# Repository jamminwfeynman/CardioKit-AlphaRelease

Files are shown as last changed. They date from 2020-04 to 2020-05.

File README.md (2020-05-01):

# CardioKit-AlphaRelease
The public release of these and many more documents is a very active work in progress. The files currently present are enough to manufacture and operate the platform. That said, I am still working on documenting all of my 'institutional knowledge' that I know is just as necessary for making the platform operate as it should. 

Please feel free to reach out if you have an urgent application or desire to collaborate in the meantime.

<p align="center">
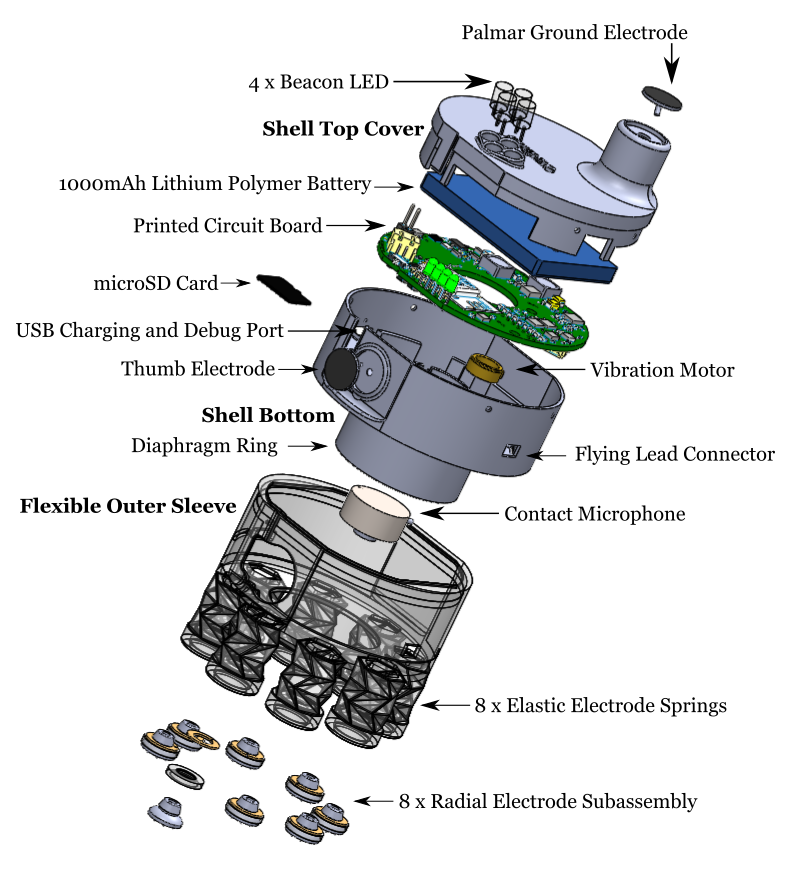
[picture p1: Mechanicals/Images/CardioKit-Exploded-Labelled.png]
  

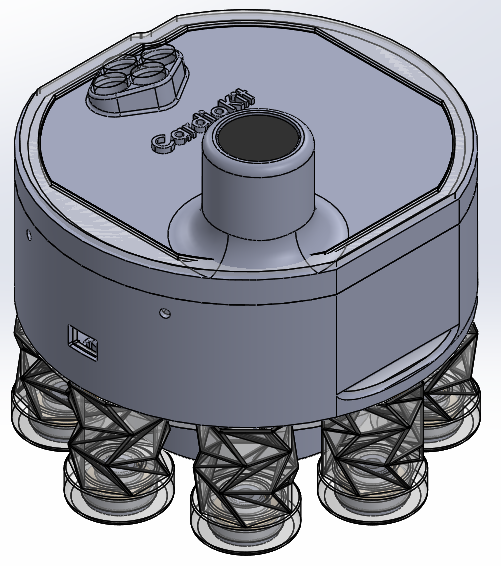
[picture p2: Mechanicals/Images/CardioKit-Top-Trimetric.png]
  

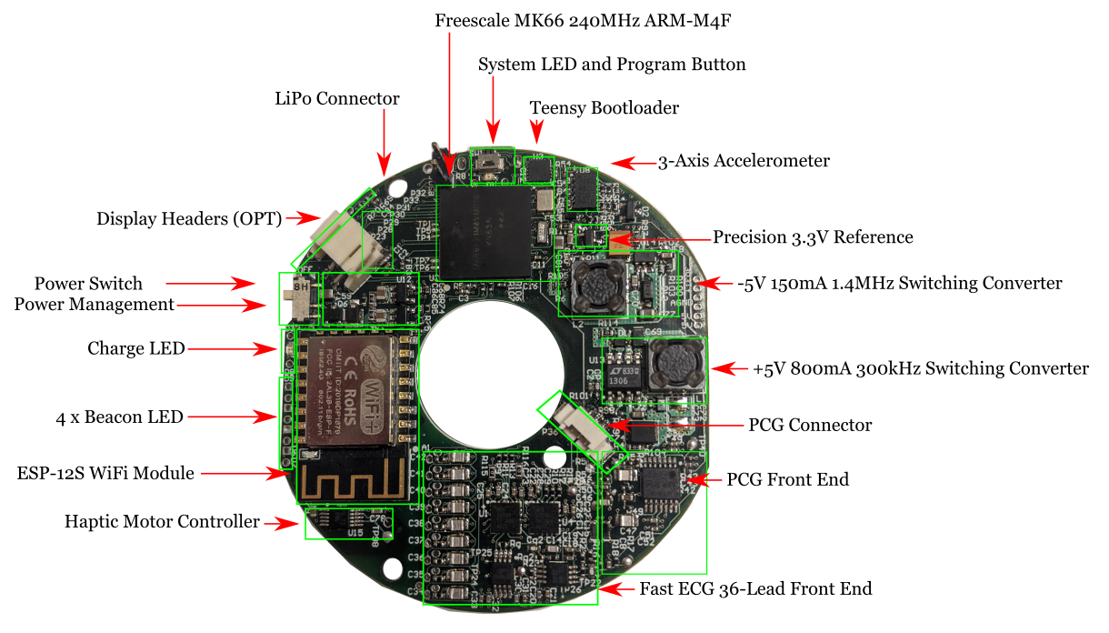
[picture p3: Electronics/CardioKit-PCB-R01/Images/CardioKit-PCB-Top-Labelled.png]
  

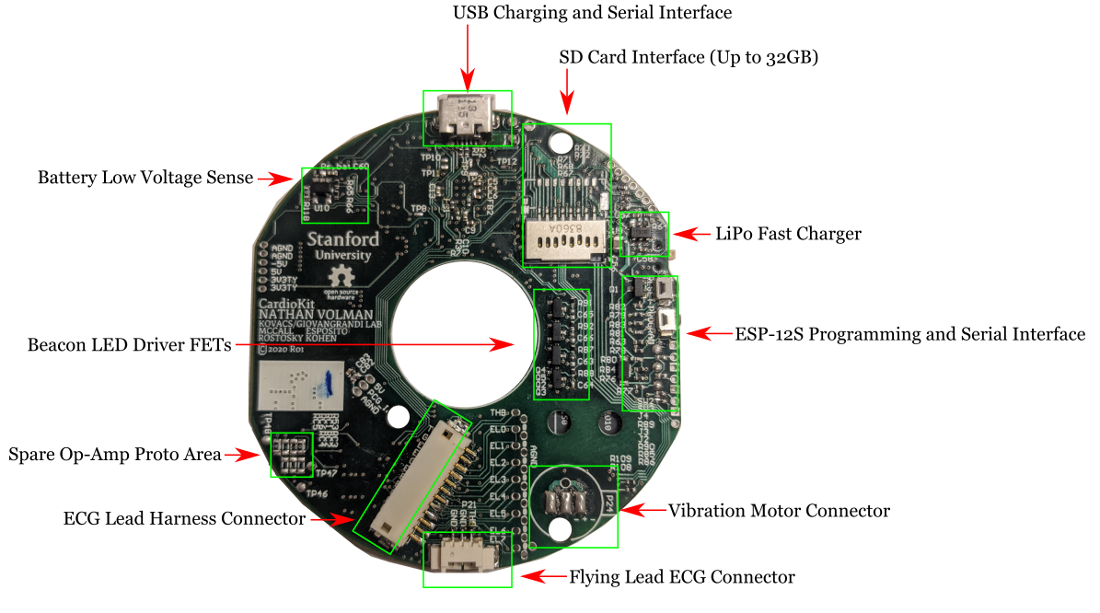
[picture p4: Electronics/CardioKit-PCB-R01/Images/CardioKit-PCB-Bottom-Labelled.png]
  
</p>

## Quickstart Guide
- Order the CardioKit PCB R10 with assembly services using the parts in the BOM. These should be 1.6mm thick and use ENIG surface plating. Order quantity 1 per finished device.
- Order PCB Electrode Holders along with the main PCB. These should be 0.6mm thick and use ENIG surface plating. Order quantity 10 per finished device.
- Using FormLabs Form 2 with Elastic Resin or a 3D printing service with access to the same, per device print one Flexible Sleeve and eight Flexible Electrode Holders. These can be printed at the same time and also in batches of at least 2 sets at a time using the Form 2.
- Using FormLabs Form 2 with any colored resin of your choice (e.g. Grey Resin) or a 3D printing service with access to the same, per device print one Bottom Shell and one Top Shell. These can be printed at the same time and also in batches of at least 2 sets at a time using the Form 2.
- Using the Arduino IDE, Atom with PlatformIO, or your favorite C/C++ IDE import the CardioKit Firmware and upload it to each device over the USB port. Note: you will need to have Teensyduino installed before uploading.
- Following the instructions in the readme, flash the ESP8266 module with esp-link. This will require an FTDI cable attached to the ESP8266 programming headers on the underside of the PCB.
- Assemble PCB, sensors, battery, vibration motor, and housing together into the completed device. (More detailed build guide coming soon).
- For local network use: Using Processing of Java Eclipse, import the CardioKit Host Software. With the device enabled, enter its IP address and run the software to automatically connect.
- For cloud use: Spin up an instance on AWS and follow the directions above. Note: you may need to bypass your network's firewall to successfully connect. (More details coming soon).
- That's it! All signals recorded by the device will be stored in a csv for post-processing at the end of each session. Example signal importation and post-processing can be seen in this Matlab script.

## To-Do
- Clean-up, optimization, repackaging of firmware
- Clean-up, optimization, repackaging of cloud software
- Detailed description of performance and capabilities
- Detailed build guide
- Tips for self-assembly of pcb and sourcing of parts
- Initial commits of most of the post-processing code
- Tips for getting good results from 3D printer and description of process
- Detailed guide for extending FW/SW/HW/Mechanicals
- Much more...

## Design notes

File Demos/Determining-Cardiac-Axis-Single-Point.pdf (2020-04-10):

## Determining Cardiac Axis from a Single Point

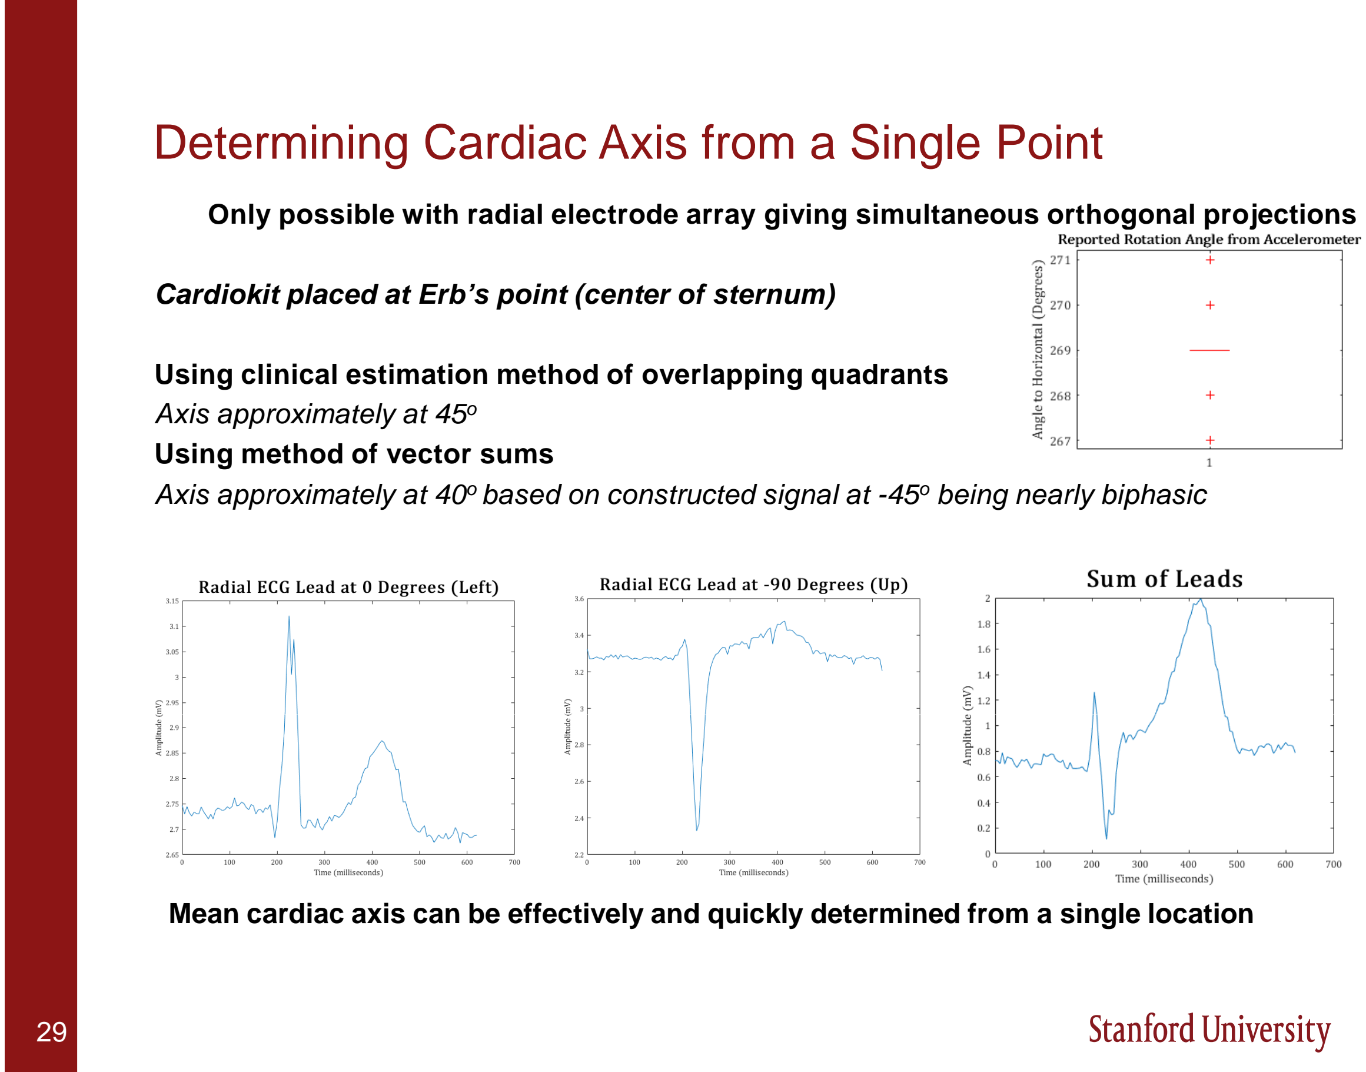
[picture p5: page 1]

Only possible with radial electrode array giving simultaneous orthogonal projections

Cardiokit placed at Erb’s point (center of sternum)

Using clinical estimation method of overlapping quadrants
Axis approximately at 45
o
Using method of vector sums
Axis approximately at 40o based on constructed signal at -45

o being nearly biphasic

29

Mean cardiac axis can be effectively and quickly determined from a single location

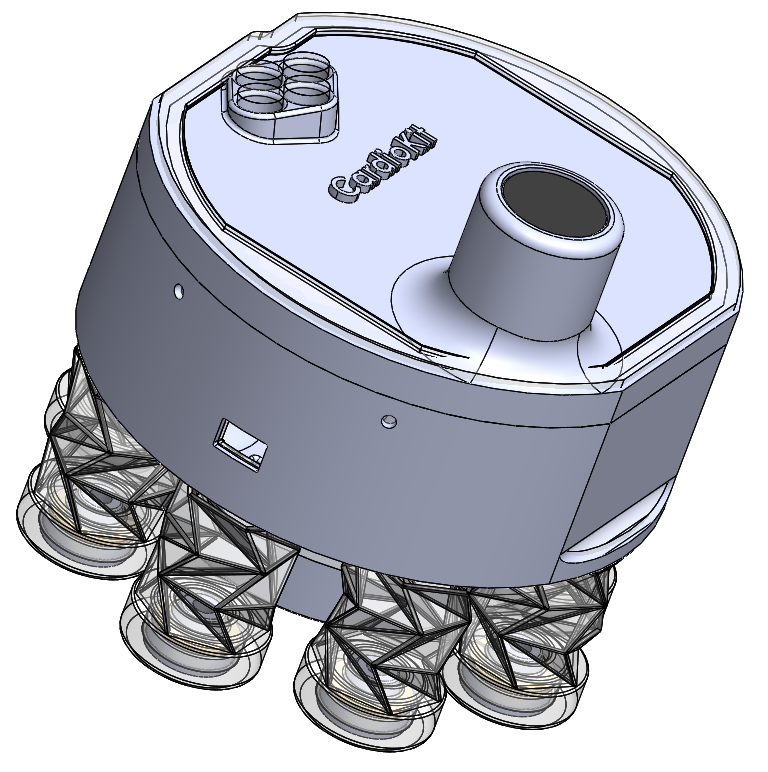
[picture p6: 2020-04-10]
Mechanicals/Images/CardioKit-Top.png

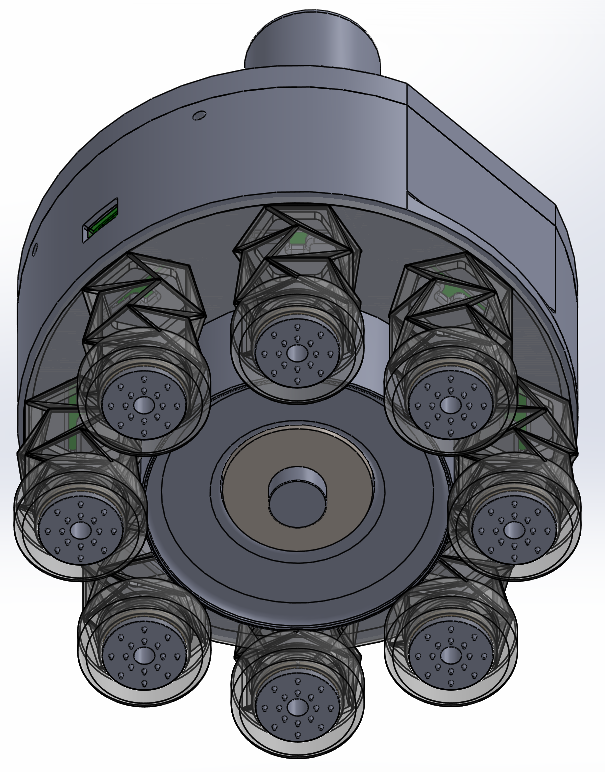
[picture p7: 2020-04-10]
Mechanicals/Images/CardioKit-Bottom-Trimetric.png

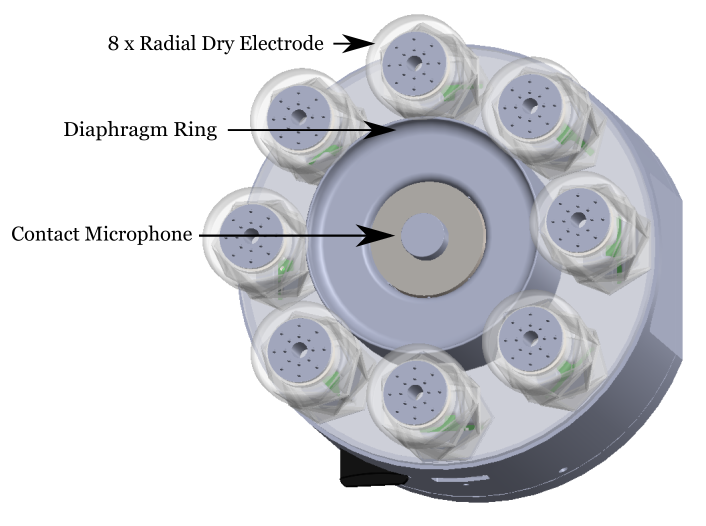
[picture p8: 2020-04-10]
Mechanicals/Images/CardioKit-Bottom-Labelled.png

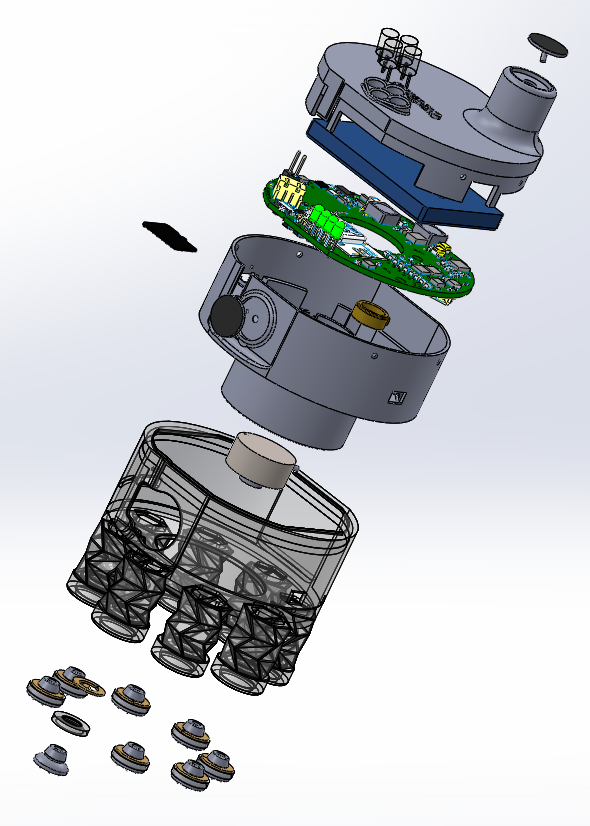
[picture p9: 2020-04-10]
Mechanicals/Images/CardioKit-Exploded.png

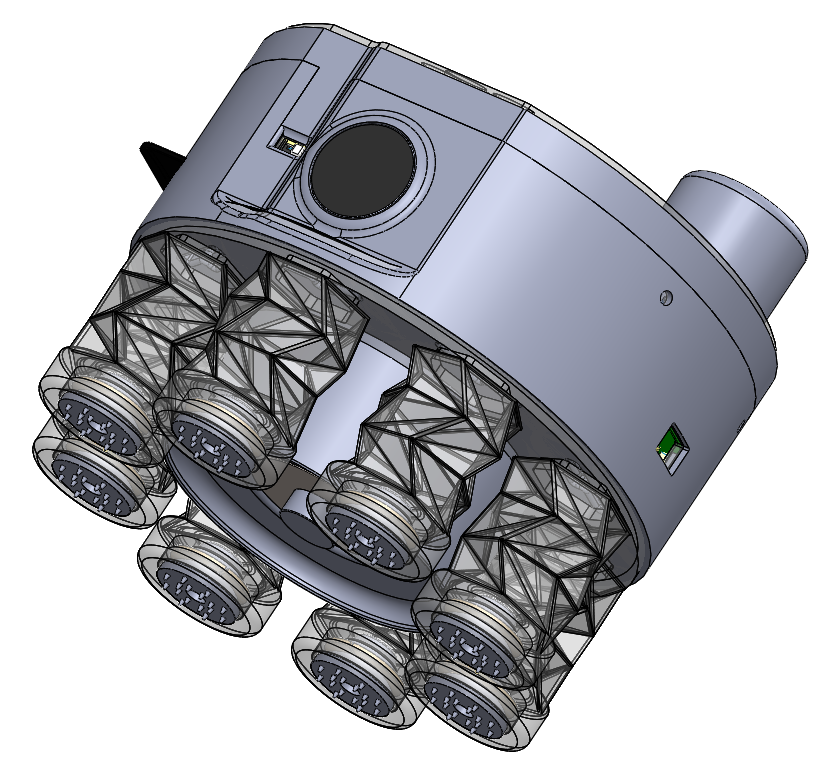
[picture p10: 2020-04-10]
Mechanicals/Images/CardioKit-Thumb-Side.png

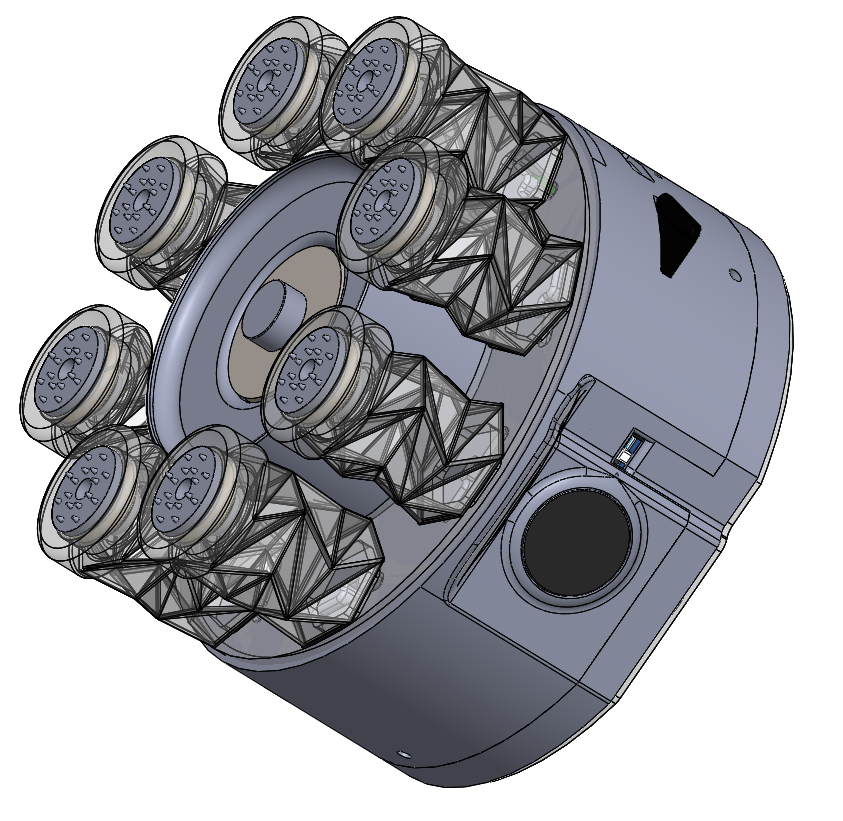
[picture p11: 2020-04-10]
Mechanicals/Images/CardioKit-PCG-Electrodes.png

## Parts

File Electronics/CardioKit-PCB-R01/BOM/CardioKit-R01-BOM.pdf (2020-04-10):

Comment | Description | Designator | Manufacturer Part Number | Quantity
0.1uF | CL05 Series 0.1 uF 16 V ±10% Tolerance X7R SMT Multilayer Ceramic Capacitor

C1, C4, C8, C10, C11, C12, C13, C19, C21, C23, C25, C27, C29, C31, C33, C43, C50, C52, C54, C55, C57, C58, C60, C63, C64, C65, C66, C75, C83, C84, C85, C86

CL05B104KO5NNNC | 32
110pF 5% C0G | CAP CER 110PF 50V 5% NP0 0402 | C7, Cg2 | C0402C111J5GAC7867 | 2
2nF 5% C0G | CAP CER 2000PF 50V 5% NP0 0603 | C14, C46 | GRM1885C1H202JA01D | 2
100pF | Cap Ceramic 100pF 50V C0G 5% SMD 0402 125°C Cardboard T/R | C18, C20, C22, C24, C26, C28, C30, C32, C49, C51, C82 | CL05C101JB5NNNC | 11
10nF 16V 2% PPS | Capacitor 0.01 uF 16 Volt PLYPH 2% 2 X 1.25 X 1.1mm Surface Mount Tape and Reel | C34, C35, C36, C37, C38, C39, C40, C41, C42, C44, C47 | ECH-U1C103GX5 | 11
15nF 5% | CAP CER 0.015UF 35V NP0 0603 | C45 | C1608C0G1V153J080AC | 1
240pF 5% C0G | Multilayer Ceramic Capacitors MLCC - SMD/SMT 240pF 50Volts C0G 2% | C48 | C0402C241J5GAC7867 | 1
10uF 16V | Cap Multilayer Ceramic 0805 10uF 16V ±10% X7R CL21 Series | C56, C59, C62, C67, C81 | CL21B106KOQNNNG | 5
1uF 16V | CAP CER 1UF 16V X7R 0603 | C70, C76, C78, C79, C80 | CL10B105MO8NNWC | 5
22uF Tant | Cap Tant Solid 10uF 10V B CASE 10% (3.5 X 2.8 X 1.9mm) Inward L SMD 3528-21 2.5 Ohm 125C T/R | C71 | TAJB106K010RNJ | 1
220uF | Cap Tant Solid 220uF 6.3V B CASE 20% (3.5 X 2.8 X 1.9mm) SMD 3528-21 0.045 Ohm 105°C T/R | C72, C74 | T520B227M006ATE045 | 2
68pF | Cap, 68Pf, 25V, 5%, C0g/Np0, 0402 | CP | 8.85E+11 | 1
68nF | Cap Cer 0.068UF 16V X7R 0402 | CZ | CC0402KRX7R7BB683 | 1
1200pF 10% | CAP CER 1200PF 100V 5% X7R 0603 | C_NFB | CL10B122KB8NNNC | 1
BAV70LT1G | Dual Switching Diodes, Common Cathode, 3-Pin SOT-23, Pb-Free, Tape and Reel | D2 | BAV70LT1G | 1
MBR120 | MBR120LSFT Series 20 V 1 A Surface Mount Schottky Power Rectifier - SOD-123FL | D5 | MBR120LSFT1G | 1
Bourns SRF0703-220M | Ind Power Shielded Wirewound 10uH/40uH 20% 100KHz Ferrite 2.08A/1.04A T/R | L1, L2 | SRF0703-220M | 2
Hirose DF13-12P-1.25H(76) | DF13 Series 12 Position Single Row 1.25 mm Right Angle SMT Pin Header | P6 | DF13-12P-1.25H(76) | 1
Molex 53261-0371 | Conn Shrouded Header HDR 3 POS 1.25mm Solder RA SMD PicoBlade Embossed T/R | P21, P36 | 53261-0371 | 2
RK7002BM | N-Channel 60 V 0.2 W Surface Mount 2.5 V Drive Silicon Power Mosfet - SOT-23 | Q1, Q2, Q3, Q4, Q5 | RK7002BMT116 | 5
0R | Res Thick Film 0603 0 Ohm Molded SMD SMD Punched Carrier T/R | R4, R6, R53, R54, R69, R70, R94, R97,
| | R110, R111, R113, R114, R115, R116,
| | R117, R118, RC5 | ERJ-3GEY0R00V | 17
1k 1% | YAGEO (PHYCOMP) RC0402FR-071KL RESISTOR, RC32H 0402 1K

R9, R10, R11, R12, R13, R14, R44, R55,
R57, R58, R59, R61, R62, R67, R68, R71,
R72, R73, R74, R76, R77, R82, R87, R88, R91, R92, R108, R109
RC0402FR-071KL | 28
10k2 1% | Thick Film Resistors - SMD 10.2K OHM 1% | R15, Rg2 | RC0402FR-0710K2L | 2
3k4 1% | Thick Film Resistors - SMD 3.4K OHM 1% | R16 | RC0402FR-073K4L | 1
17k8 1% | Thick Film Resistors - SMD 17.8K OHM 1% | R17 | RC0402FR-0717K8L | 1
10k7 1% | RES SMD 10.7K OHM 1% 1/16W 0402 | R18 | RC0402FR-0710K7L | 1
442R 1% | Thick Film Resistors 442 OHM 1% | R21, R22 | RMCF0402FT442R | 2
560R 1% | RES SMD 560 OHM 1% 1/16W 0402 | R23 | RC0402FR-07560RL | 1
100k 0.1% | RES SMD 100K OHM 0.1% 1/16W 0402 | R24, R25, R26, R27, R28, R29, R30, R31, R32, Rs,bat | RNCF0402DTE100K | 10
162k 1% | Thick Film Resistors - SMD 0402 162Kohms 1% Tol | R42, R43, R51 | RC0402FR-07162KL | 3
4k42 1% | Thick Film Resistors - SMD 4.42K OHM 1% | R45, R48, R50 | RC0402FR-074K42L | 3
6k65 1% | Thick Film Resistors 6.65K OHM 1% | R49 | RC0402FR-076K65L | 1
232k 1% | Thick Film Resistors - SMD 0402 232Kohms 1% Tol | R52 | RC0402FR-07232KL | 1
10k | Res Thin Film 0402 10K Ohm 0.5% 0.063W(1/16W) ±25ppm/C Molded SMD Automotive Punched T/R | R56, R60, R65, R75, R78, R79, R80, R81, R83, R84, R95, R102, R103 | RMCF0402FT10K0 | 13
2k2 5% | RES SMD 2.2K OHM 5% 1/16W 0402 | R63, R106, R107 | RC0402JR-072K2L | 3
1k1 | RES SMD 1.1K OHM 1% 1/16W 0402 | R64 | CRCW04021K10FKED | 1
1M65 1% | Thick Film Resistors - SMD 1.65M OHM 1% | R66 | RMCF0402FT1M65 | 1
91R 5% | Thick Film Resistors - SMD 91 OHM 5% | R85, R86, R89, R90 | RMCF0402JT91R0 | 4
768k | Thick Film Resistors - SMD 0402 768Kohms 1% Tol | R98 | ERJ-2RKF7683X | 1
249k | RES SMD 249K OHM 1% 1/16W 0402 | R99 | MCR01MRTF2493 | 1
29k4 | Thick Film Resistors - SMD 29.4K OHM 1% | R100 | RC0402FR-0729K4L | 1
118k | RES SMD 118K OHM 1% 1/16W 0402 | R101 | CRCW0402118KFKED | 1

100R 5% 1/4W | Res Thick Film 0603 100 Ohm 5% 1/4W +/-200ppm/ßC Molded SMD SMD Paper T/R | R104, R105 | ESR03EZPJ101 | 2
1k5 0.1% | RES SMD 1.5K OHM 0.1% 1/16W 0402 | Rg | RT0402BRD071K5L | 1
MUX36S08 | 36-V, low-capacitance, low-leakage-current, precision, analog multiplexer 16-WQFN -40 to 125 | U1, U4 | MUX36S08IRRJR | 2
OPA2141 | 10 MHz, Single Supply, Low Noise, JFET Precision Amplifier, 4.5 to 36 V, -40 to 125 degC, 8-pin SOP (DGK8), Green (RoHS & no Sb/Br) | U5 | OPA2141AIDGKT | 1
AD8220 | SP Amp Instrumented Amp Single Rail to Rail O/P ±18 Volt 36 Volt 8-Pin MSOP | U6 | AD8220BRMZ | 1
OPA4141 | 10 MHz, Single Supply, Low Noise, JFET Precision Amplifier, 4.5 to 36 V, -40 to 125 degC, 14-pin SOP (PW14), Green (RoHS & no Sb/Br) | U7 | OPA4141AIPW | 1
ADXL345 | 3-Axis, +/-2 g / +/-4 g / +/-8 g / +/-16 g Digital Accelerometer with Digital Output, 1.6 KHz BW, Industrial, 14-
| pin LGA, Tray | U8 | ADXL345BCCZ | 1
MIC7221 | MIC7221 Series Single 10 V 0.5 pA IttyBitty? Rail-to-Rail Comparator - SOT-23-5 | U10 | MIC7221 | 1
DRV2605L | Haptic Driver for ERM and LRA with Built-In Library and Smart Loop Architecture 10-VSSOP -40 to 85 | U15 | DRV2605L | 1
REF3333AIDBZR | 30 ppm / degC Drift, 3.9 uA Voltage Reference, -40 to 125 degC, 3-pin SOT-23 (DBZ), Green (RoHS & no Sb/Br) | U16 | REF3333AIDBZR | 1
3-Terminal Pico Blade Female Wire-To-Board | | | ?0510210300? | 2
Pico Blade Crimp Connector | | | ?0500588000? | 6
Hirose Female Wire-To-Board | | | DF13-12S-1.25C? | 1
Hirose Low Insertion Force Gold Crimp Pin | | | DF13G-2630SCFA? | 12
LED | LED; Red; 30mcd; 0.126In.Dia.; T-1; 150mA; 2V; 635nm; 60deg; Diffused; 85 to 85degC | D4, D6, D7, D8, D9 | OVLLR8C7 | 5
ESP-12S | ESP-12S | A1 | | 1
CM-01B
100k DNP | THIN FILM, RESISTOR, 100KOHM, 63mW, ±0.5% | R5 | ERA-2AED104X | 1
10M 1% | YAGEO (PHYCOMP) RC0402FR-0710ML RESISTOR, 0402 0.063W 1% 10M | R33, R34, R35, R36, R37, R38, R39, R40, R41 | RC0402FR-0710ML | 9
310-105 | Precision Microdrives 310-105 10mm Vibration Motor - 4mm Type | P24 | 310-105 | 1
Omron B3U-3000P | TACTILE SWITCH, SIDE ACTUATED, SMD | SW1,SW2,SW3 | B3U-3000P | 1
MKL02Z32VFG4 | 32 Bit Microcontroller, Kinetis L Series Ultra Low Power, ARM Cortex-M0+, 48 MHz, 32 KB, 4 KB, 16 | U3 | MKL02Z32VFG4 | 1
LiPo | 2 Positions Header, Shrouded Connector 0.079 (2.00mm) Surface Mount | BT1 | S2B-PH-SM4-TB(LF)(SN) | 1
Microsemi UPS115UE3/TR7 | Standard Recovery Diode And Rectifier | D10 | UPS115UE3/TR7 | 1
33R | Thick Film Resistors - SMD 1/16W 33ohm 1% | R1, R2 | AC0402FR-0733RL | 2
120 | Chip Ferrite Bead for Power Lines, 120 Ohm, 2000 mA, -55 to 125 degC, 1 x 0.5 x 0.55 mm SMD, Tape and Reel | FB3, FB4 | BLM15PX121SN1D | 2
600 | Chip Ferrite Bead for Power Lines, 600 Ohm, 900 mA, -55 to 125 degC, 1 x 0.5 x 0.55 mm SMD, Tape and Reel | FB1, FB2 | BLM15PX601SN1D | 2
470R | Thick Film Resistors - SMD 0402 470ohms 5% Tol, Thick Film Resistors - SMD 0402 470ohms 5% Tol, RES SMD 470 OHM 1% 1/16W 0402 | R3, R7, R8 | ERJ-2GEJ471X, ERJ-2GEJ471X, CRCW0402470RFKED | 3
32.768kHz | Crystal 0.032768MHz ±20ppm (Tol) 12.5pF Flexural 50000Ohm 2-Pin SMD T/R | X2 | TFE322P32K7680R | 1
LT1306 | LT1306 - Synchronous, Fixed Frequency Step-Up DC/DC Converter | U13 | | 1
LT1611 | Inverting 1.4 MHz Switching Regulator, 5-pin SOT23 (S5-5), 0 to 70 degC, Pb-Free, Tape and Reel | U14 | LT1611CS5#TRPBF | 1
NXP Semiconductors MK66FX1M0VMD18 | Kinetis K66: 180MHz Cortex-M4F MCU, 1.2MB Flash, 256KB SRAM, 2xUSB, Ethernet, 144-MAPBGA | U2 | MK66FX1M0VMD18 | 1
BQ21040 | 0.8A Single Input Single-Cell Li-Ion and Li-Pol Battery Charger 6-SOT-23 0 to 125 | U9 | | 1
16MHz | CRYSTAL 16MHZ 8PF SMD | X1 | NX3225SA-16.000MHZ-STD-CSR-1 | 1
Micro SD Card Connector | Conn Micro SD Card HDR 8 POS 1.09mm Solder RA SMD Embossed T/R 0.5A | P1 | 1051620001 | 1
1uF | Cap Tant Polymer 1uF 35VDC W9 CASE 20%( 2 X 1.25 X 0.9mm) SMD 2012-09 0.5 Ohm 105C T/R | C69 | T58W9105M035C0500 | 1
MMDL914T3G | High-Speed Switching Diode, 2-Pin SOD-323, Pb-Free, Tape and Reel | D11 | MMDL914T3G | 1
MBR0520 | Rectifier, Schottky Power; Plastic Sod-123; 0.5 a @ +90c If; +125; 20v; 1000 | D12 | MBR0520LT1G | 1
22uF | Cap Tant Polymer 22uF 10VDC M CASE 20%( 1.6 X 0.85 X 1mm) Undertab SMD 1608-09 0.5 Ohm 60C T/R | C73 | F381A226MMAAXE | 1
22uF 6.3V | Cap Ceramic 22uF 6.3V X5R 10% SMD 0805 85°C Cardboard T/R | C77 | CL21A226KQCLRNC | 1
SSM3J328R | Trans MOSFET P-CH Si 20V 6A 3-Pin SOT-23F | Q6 | SSM3J328R | 1
LP5907QMFX-3.3 | IC REG LDO 3.3V 0.25A SOT23-5 | U11, U12 | LP5907MFX-3.3/NOPB | 2
CUS-12TB | Switch Slide SPDT Side Slide 0.3A 20VDC Gull Wing SMD Embossed T/R | SW4 | CUS-12TB | 1
USB microB | MICRO USB AB, RECEPTACLE, TOP MOUNT | J1 | 47590-0001 | 1
2.2uF | Multilayer Ceramic Capacitor, GRM Series, 2.2 F, 10%, X5R, 10 V, 0402 [1005 Metric] | C2, C3, C9, C16, C61, C68 | GRM155R61A225KE95D | 6
10nF | Cap Ceramic 0.01uF 16V X7R 10% SMD 0402 125°C Paper T/R | C5, C6 | C0402C103K4RECAUTO | 2
10uF Tant | 10µF Molded Tantalum Polymer Capacitor 10V 0603 (1608 Metric) 300mOhm @ 100kHz | C15, C17, C53 | F381A106MMAAH1 | 3

LED | SMD mono-color Chip LED, WL-SMCW, Super Red | D1,D3 | 150060SS75000 | 1

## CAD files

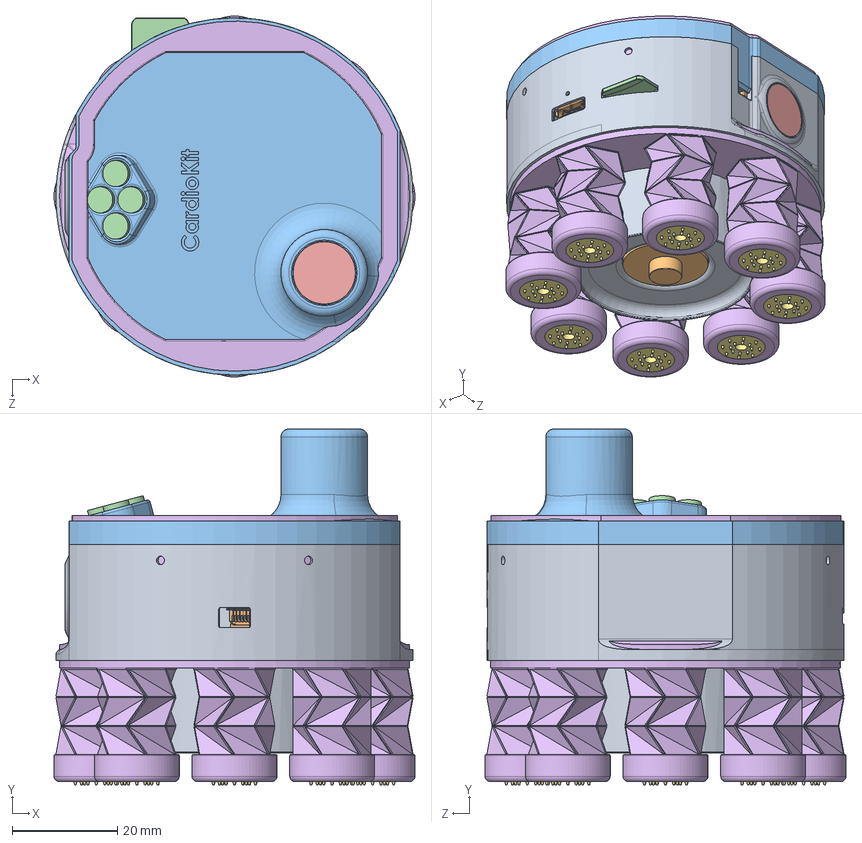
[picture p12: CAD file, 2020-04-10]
Mechanicals/CardioKit-Full-Assembly-R20/CardioKit-Full-Assembly-R20.SLDASM
68.7 x 67.7 x 68.7 mm
CardioKit_Shell_R00
CardioKitPCB_R01
CardioKit_Shell_Top_R30
LED_5mm x 4
Sintered12mmElectrode x 2
CardioKit_Sock_R30
SpikedElectrodes x 8
ElectrodeHolder x 8
Spring_R20_1pt7mmFinal2_Narrower x 8
MeasurementSpecialties_CM_01B
310-105_PrecisionMicrodrives
Micro SD Card
Tenergy_1000mAh_RectangularLiPo

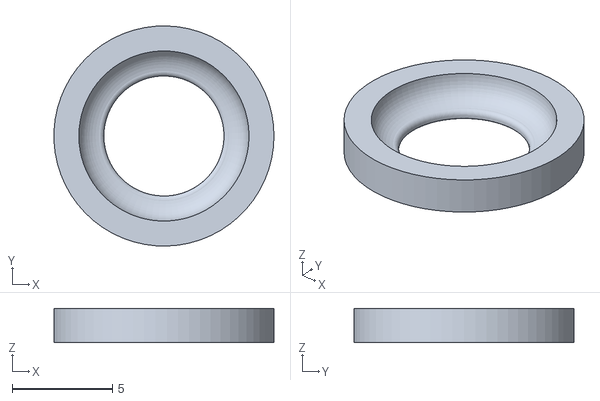
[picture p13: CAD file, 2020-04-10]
Mechanicals/CardioKit-Electrode-Holder-R50/Production-Files/CardioKit-Electrode-Holder-R50.STL
11.0 x 11.0 x 1.70

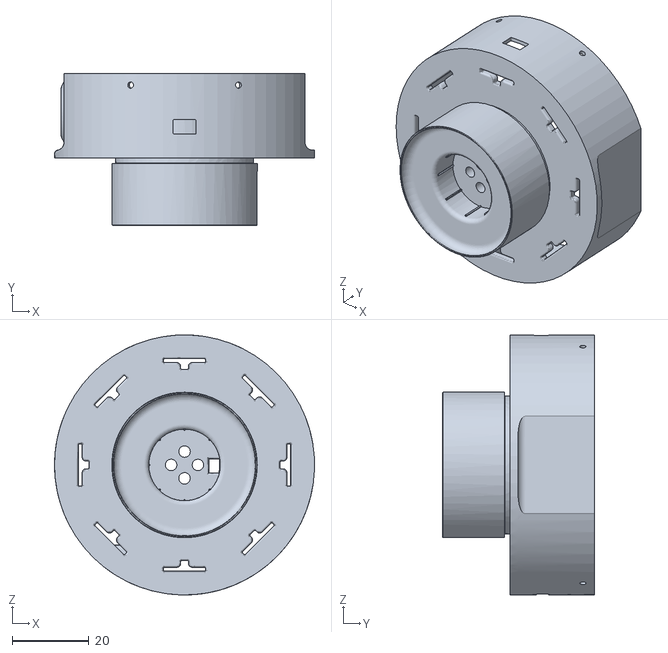
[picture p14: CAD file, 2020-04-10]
Mechanicals/CardioKit-Shell-Bottom-R30/Production-Files/CardioKit-Shell-Bottom-R30.STL
67.9 x 39.6 x 67.9

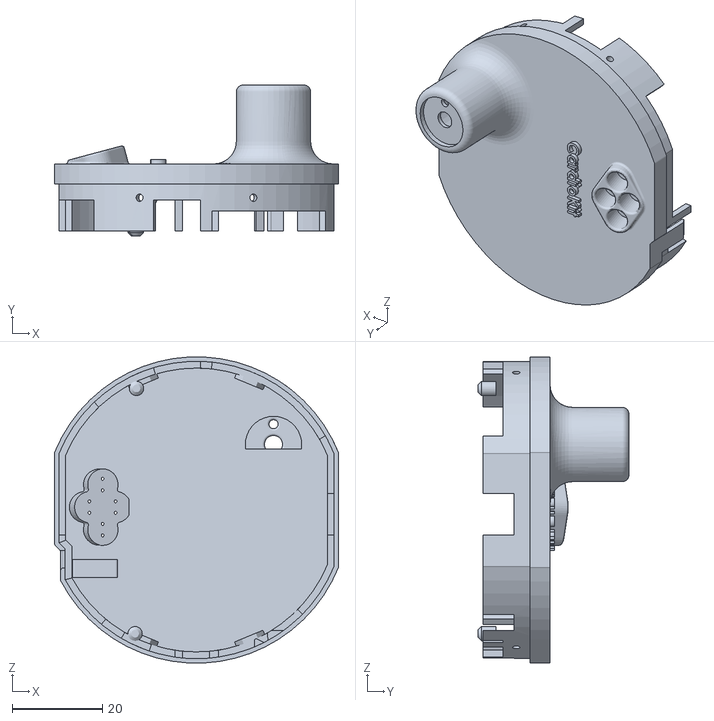
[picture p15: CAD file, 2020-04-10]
Mechanicals/CardioKit-Shell-Top-R31/Production-Files/CardioKit-Shell-Top-R31.STL
63.0 x 33.5 x 67.9

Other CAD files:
Mechanicals/CardioKit-Electrode-Holder-R50/Solidworks-Design-Files/CardioKit-Electrode-Holder-R50.SLDPRT
Mechanicals/CardioKit-Shell-Top-R31/Solidworks-Design-Files/CardioKit-Shell-Top-R31.SLDPRT

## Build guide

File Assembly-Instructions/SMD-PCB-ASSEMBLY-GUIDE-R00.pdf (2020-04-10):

## SMD PCB ASSEMBLY GUIDE Rev 0.0

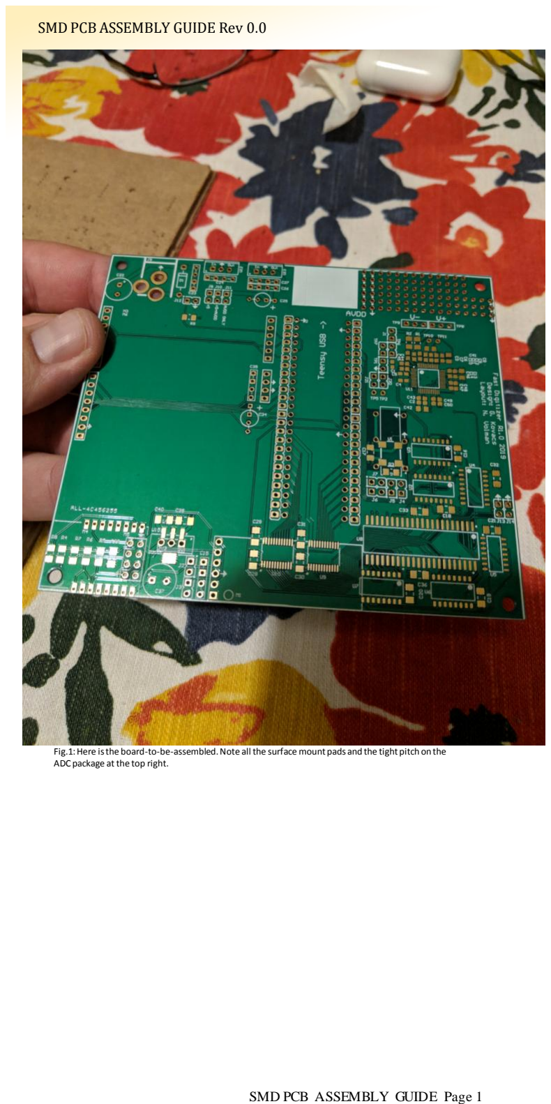
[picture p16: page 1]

Fig.1: Here is the board-to-be-assembled. Note all the surface mount pads and the tight pitch on the ADC package at the top right.

### SMD PCB ASSEMBLY GUIDE Page 1

Fig.2: Using a piece of rigid and easily workable plastic , the board-to-be-assembled is mounted approximately in the middle and surrounded on all four sides with scrap boards of identical height. Holes are then drilled and those surrounding boards screwed firmly in place making sure that the screws will not interfere mechanically with the SMD stencil being used. The only thing holding the board to be assembled in place is pressure on all four sides from the scrap boards. Where screws cannot be used (as on the leftmost donor board), generous amounts of low-profile tape are used to secure it while making sure to press the tape down very firmly on all sides.

Fig.3: The stencil is then positioned over the assembly and aligned by hand. It is easy to know when it is aligned properly because the shiny gold pads will be visible through every hole when finished. After gross alignment is complete, mounting holes are drilled through the thin metal stencil and plastic mounting board. Scrap boards (again of identical height) are placed between the stencil and the plastic mounting board (see Fig. 2 on the left). This will ensure that there is a consistent height across the entire stencil which will be critical for proper solder paste application later.

Importantly, the screw diameter used for mounting must be smaller than the mounting holes drilled for them. The play between the mounting holes and the screws comprise the only X -Y adjustment in this assembly. Each board to be assembled will have some tolerance in X and Y in the distance of the pads to the edges of the board. This is due to the boards being routed out slightly unevenly with a typically up -to ten mil difference in either direction. To account for this, for every board to be assembled, the
alignment of the stencil to the pads on that board must be checked. If the alignment is slightly off due to routing tolerances (as described earlier), the screws on the left of the assembly must be loosened. This will allow for small adjustments to be made. Once the alignment is again perfect, the nuts must be tightened down again to secure the stencil position.

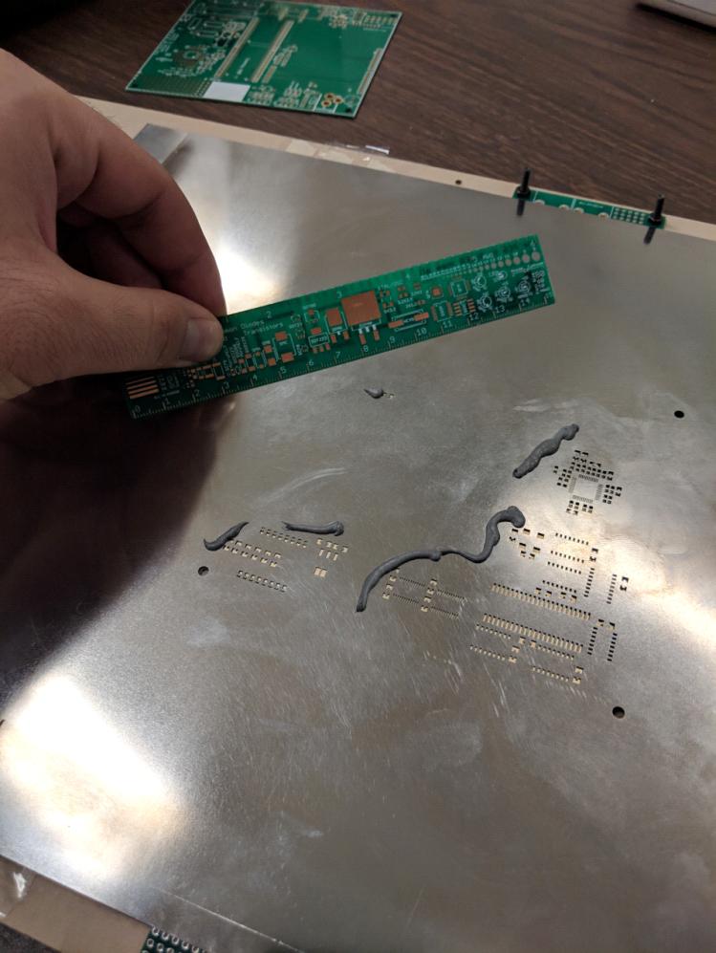
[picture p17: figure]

Fig.4: With the board held securely in place and the stencil aligned perfectly to the pads, it is now time to apply the solder paste. An ample amount of fresh solder paste is applied to the stencil to the left and up from the pads to be covered. Then, while holding the stencil tight to the board-to-be-assembled with your non-squeegee hand, squeegee the solder paste into the pads at a 45 degree angle relative to the pads. The squeegee must be thin, flexible, and straight. Here, a 0.8mm thick PCB ruler is used. Important to note is that the bottom edge of the squeegee should be held at a shallow (~30 degree angle) to the stencil such that the bottom edge trails the top edge. This will prevent the squeegee from pulling paste out of the pads once it has been applied. It is critical to hold the stencil flush against the board the entire time that paste is being applied as the distance between the pads and the top of the stencil determines the dose of paste that will be present on each pad. Too high of a dose will lead to solder bridges and short circuits.

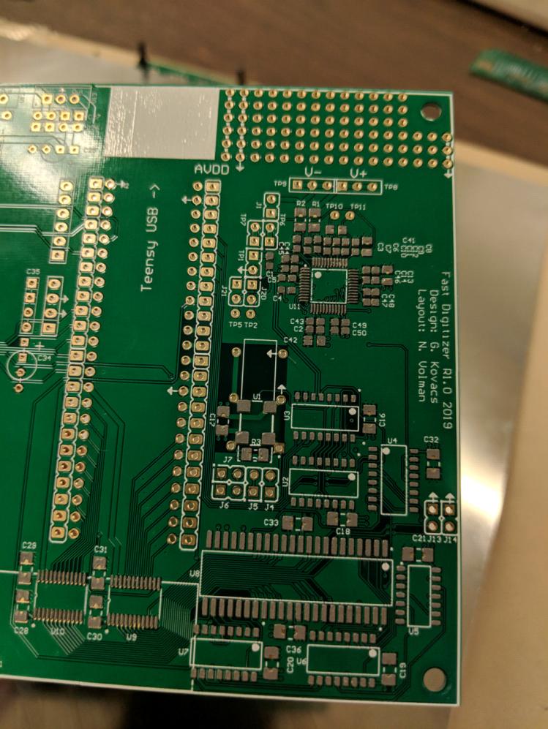
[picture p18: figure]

Fig.5: Once the paste has been applied, the stencil should be very carefully peeled back from the board -to-be-assembled. A visual inspection should then be performed to ensure that the alignment and the dose was correct. Special attention should be paid to any small features such as the pads on the Quad Flat Package (QFP) on the top right of the board. If the paste application was not successful then all paste should be removed with isopropyl alcohol and paper towels and the process restarted.

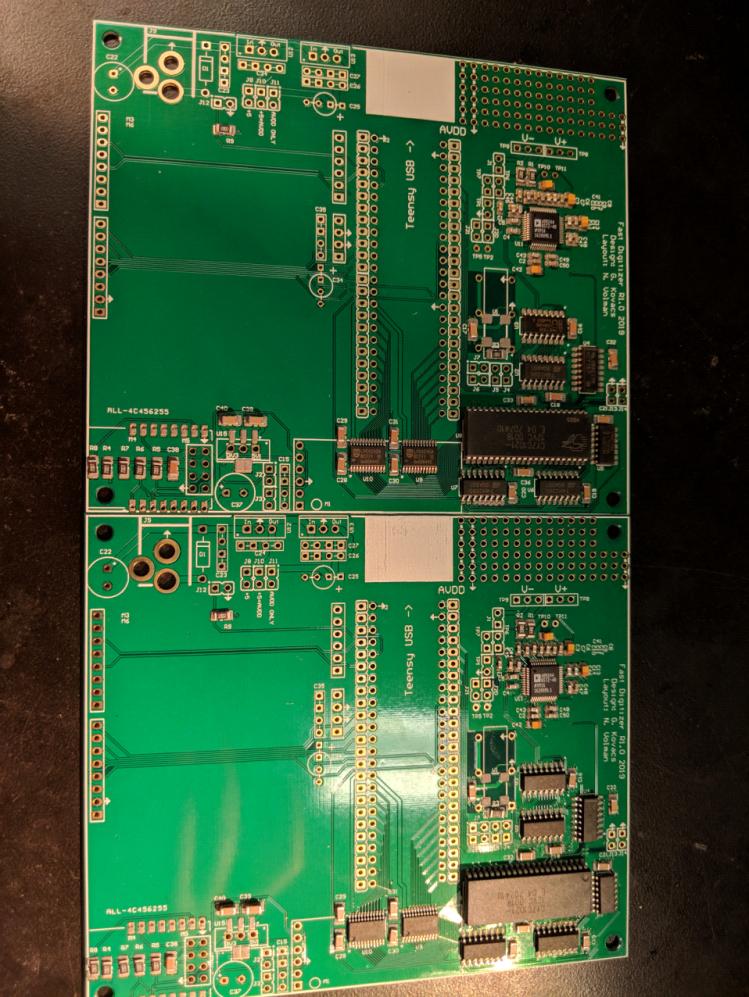
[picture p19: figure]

Fig.6: Once the board-to-be-assembled has successfully had solder paste applied, it is then time to place all SMD parts onto it. Batching this step saves a lot of time as the most time consuming part of board assembly is retrieving each individual SMD part from its respective bag and tape. The more boards being populated with parts at once, the faster assembly will go. It is important at this time not to touch or smear the solder paste that has been applied to the boards. Tweezers can be used for proper positioning of SMD parts (as shown above).

Fig.7: Once the boards have been populated entirely with their SMD components, they should be placed inside the reflow oven. The closer to the center of the oven the better as that is often where the temperature is most even.

Fig.8: With the boards inside, an appropriate thermal profile should be selected for reflow. In this case, the profile tailored to leaded solder paste was selected. Not all pads successfully reflowed after a single pass so each board inside was rotated 180 degrees and the 'wave 1' profile was re-run for a second time. This led to 100% successful reflow of all pads.

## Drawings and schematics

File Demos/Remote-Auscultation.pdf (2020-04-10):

# Listening to the Heart

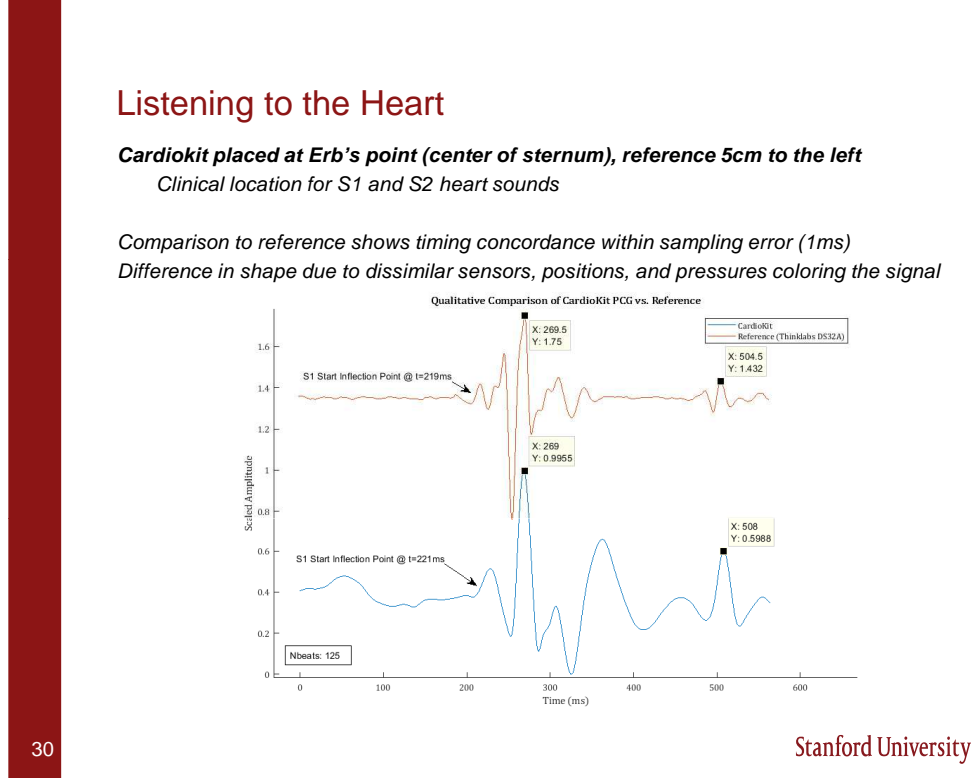
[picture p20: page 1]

Cardiokit placed at Erb’s point (center of sternum), reference 5cm to the left
Clinical location for S1 and S2 heart sounds

Comparison to reference shows timing concordance within sampling error (1ms)
Difference in shape due to dissimilar sensors, positions, and pressures coloring the signal

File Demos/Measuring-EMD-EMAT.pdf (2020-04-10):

## Application: Measuring Electromechanical Delay

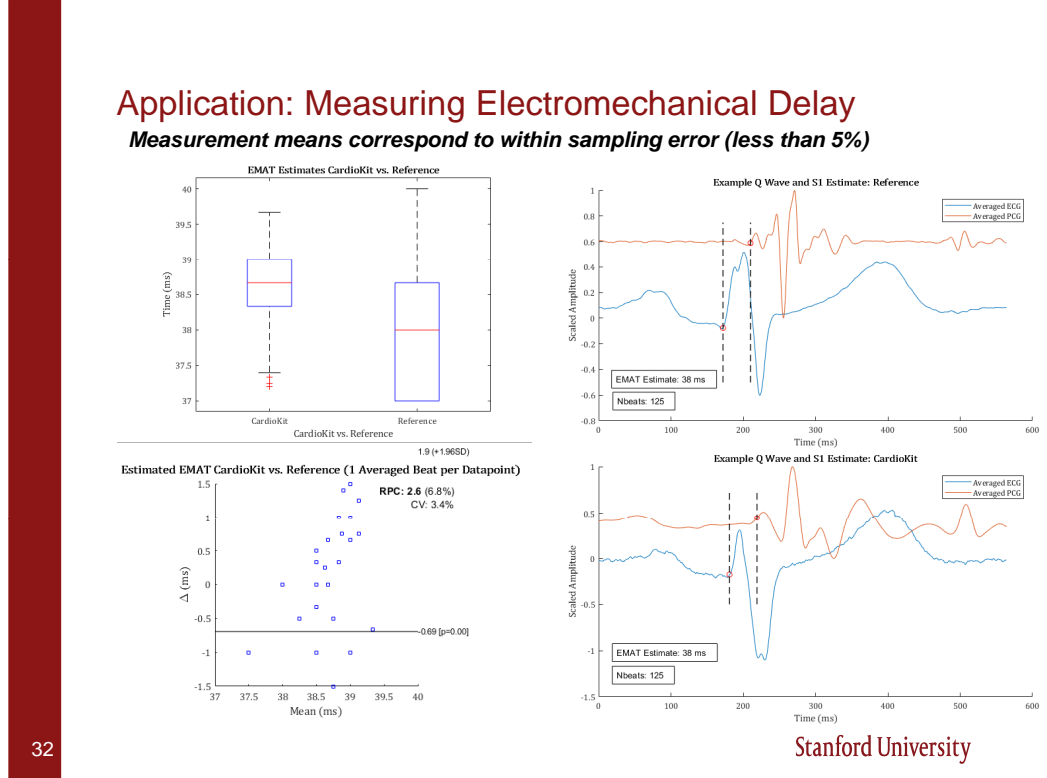
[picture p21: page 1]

Measurement means correspond to within sampling error (less than 5%)

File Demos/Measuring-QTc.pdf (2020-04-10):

## Application: Deriving Corrected QT-Interval

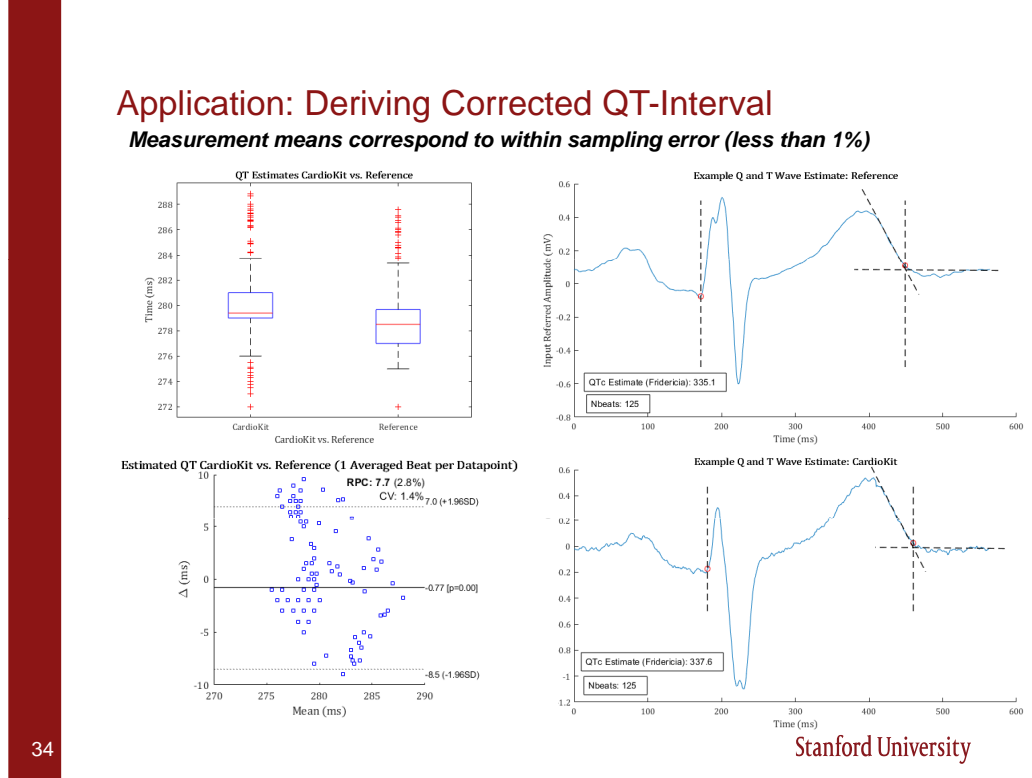
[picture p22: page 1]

Measurement means correspond to within sampling error (less than 1%)

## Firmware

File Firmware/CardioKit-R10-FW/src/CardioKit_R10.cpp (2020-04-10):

/*  *********************************************
    CardioKit_R10.cpp
    Code to run the CardioKit R01 board
    Run DC ECG DAC DMA closed-loop control
        Filter/process buffers to enable control loop
    Run Differential ADC DMA interrupt-driven sampling
    Run DC ECG MUX synchronously with DAC / ADC
    Offload data with SimpleTCP ESP8266

    Added "NVIC_ENABLE_IRQ(IRQ_PDB);" to enable pcb_isr()

    Nathan Volman
    Created: March 5, 2020
        Tested to stream properly at 240MHz fCPU
        Changed fCPU from 180MHz (default) to 240MHz consuming an extra 20mA
        Changed fCPU back to 180MHz, didn't need extra speed, not worth extra noise
    Development Environment Specifics:
    Atom + PlatformIO

    Hardware Specifications:
    See schematics for ESP-12E
    and CardioKit R01
 *  *********************************************/
#include <Arduino.h>
#include <IntervalTimer.h>
#include <ADC.h>
#include <RingBufferDMA.h>
#include "SimpleTCP.h"
#include "hwsettings.h"
#include "CardioKitDac.h"
#include "qcepMux.h"
#include "CardioKitLEDS.h"
#include "CardioKitCommandSpace.h"
#include <SparkFun_ADXL345.h>
#include <math.h>

ADC *adc = new ADC();

const uint8_t adc_dma_buffer_size = 1; // 128 is hard max, aliases down for higher numbers
DMAMEM static volatile int16_t __attribute__((aligned(adc_dma_buffer_size + 0))) bufferAdc0[adc_dma_buffer_size]; // allocate ADC0 DMA buffer
DMAMEM static volatile int16_t __attribute__((aligned(adc_dma_buffer_size + 0))) bufferAdc1[adc_dma_buffer_size]; // allocate ADC1 DMA buffer
RingBufferDMA *dmaBuffer0 = new RingBufferDMA(bufferAdc0, adc_dma_buffer_size, ADC_0); // use dma with ADC0
RingBufferDMA *dmaBuffer1 = new RingBufferDMA(bufferAdc1, adc_dma_buffer_size, ADC_1); // use dma with ADC1

//////////////////////////////////////////////
///////// INITIALIZE STATE VARIABLES /////////
//////////////////////////////////////////////
volatile static uint16_t samples[PINGPONG_BUFFER_COUNT][NUM_DATA_STREAMS][CHANNEL_BUFFER_LENGTH] = {0}; // Ping-pong Buffer 1 and 2
volatile static uint8_t  current_channel               =  0;     // Which ECG Channel is the ADC currently sampling
volatile static uint16_t samples_idx[NUM_DATA_STREAMS] = {0};    // For each Channel, what is the index into 'samples[CURR_BUF][CH_N][]'
volatile static uint8_t  buffer_num                    =  0;     // Which Ping-Pong Buffer is currently being used
volatile static uint8_t  buffer_num_pcg                =  0;     // Which Ping-Pong Buffer is currently being used by pcg
volatile static bool     buffer_ready_flag             =  false; // Signals that one of the Ping-Pong buffers is ready for processing
volatile static bool     pcg_buffer_ready_flag         =  false; // Signals that one of the Ping-Pong buffers is ready for processing
volatile static bool     accel_read_sample_flag        =  false; // Signals that the accelerometer should take another reading


//////////////////////////////////////////////
////////// ACCELEROMETER VARIABLES ///////////
//////////////////////////////////////////////
int16_t ACCELx,ACCELy,ACCELz;
ADXL345 adxl = ADXL345(pinADXL_CS); // SPI, ADXL345(CS_PIN);

// returns 0 to 359 degrees with 0 degrees being towards left shoulder, 90 towards feet, 270 towards head
FASTRUN uint16_t GetAxisAngle(int x, int y)
{
    double theta = double(y)/double(x);
    theta = atan(theta) * 180.0/ 3.14159265;
    theta = abs(theta);

    if( x >= 0 && y >= 0)
    { // both +ve
        theta = 180 + theta;
    }
    else if( x >= 0 && y <= 0)
    { // x +ve, y -ve
        theta = 180 - theta;
    }
    else if( x <= 0 && y <= 0)
    { // both -ve
        //theta = theta;
    }
    else
    { // x -ve, y +ve
        theta = 360 - theta;
    }
    uint16_t angle = (uint16_t) (theta);
    return (angle % 360);
}

FASTRUN void ReadAccelIntoArray()
{
    adxl.readAccel(&ACCELx, &ACCELy, &ACCELz);
    samples[buffer_num][ACCEL_STREAM_SLOT][samples_idx[ACCEL_STREAM_SLOT]] = GetAxisAngle(ACCELx,ACCELy);
    samples_idx[ACCEL_STREAM_SLOT] = (samples_idx[ACCEL_STREAM_SLOT] + 1) % CHANNEL_BUFFER_LENGTH; // Move samples buffer indices
}

/********************* ISR *********************/
FASTRUN void ADXL_ISR() {
    Serial.println("ADXL_ISR");
  // getInterruptSource clears all triggered actions after returning value
  // Do not call again until you need to recheck for triggered actions
  byte interrupts = adxl.getInterruptSource();

  // Free Fall Detection
  if(adxl.triggered(interrupts, ADXL345_FREE_FALL)){
    Serial.println("*** FREE FALL ***");
    //add code here to do when free fall is sensed
  }

  // Inactivity
  if(adxl.triggered(interrupts, ADXL345_INACTIVITY)){
    Serial.println("*** INACTIVITY ***");
     //add code here to do when inactivity is sensed
  }

  // Activity
  if(adxl.triggered(interrupts, ADXL345_ACTIVITY)){
    Serial.println("*** ACTIVITY ***");
     //add code here to do when activity is sensed
  }

  // Double Tap Detection
  if(adxl.triggered(interrupts, ADXL345_DOUBLE_TAP)){
    Serial.println("*** DOUBLE TAP ***");
     //add code here to do when a 2X tap is sensed
  }

  // Tap Detection
  if(adxl.triggered(interrupts, ADXL345_SINGLE_TAP)){
    Serial.println("*** TAP ***");
     //add code here to do when a tap is sensed
  }
}

FASTRUN void ADXL_ISR2() {}

void InitADXL()
{
    pinMode(pinADXL_INT1, INPUT); // Setup interrupt pins for ADXL
    pinMode(pinADXL_INT2, INPUT); // Setup interrupt pins for ADXL

    adxl.powerOn();                     // Power on the ADXL345

    adxl.setRangeSetting(2);            // Give the range settings
                                      // Accepted values are 2g, 4g, 8g or 16g
                                      // Higher Values = Wider Measurement Range
                                      // Lower Values = Greater Sensitivity (false, sensitivity is fixed at full resolution)

    adxl.setSpiBit(0);                  // Configure the device to be in 4 wire SPI mode when set to '0' or 3 wire SPI mode when set to 1
                                      // Default: Set to 1
                                      // SPI pins on the ATMega328: 11, 12 and 13 as reference in SPI Library

    adxl.setActivityXYZ(1, 0, 0);       // Set to activate movement detection in the axes "adxl.setActivityXYZ(X, Y, Z);" (1 == ON, 0 == OFF)
    adxl.setActivityThreshold(75);      // 62.5mg per increment   // Set activity   // Inactivity thresholds (0-255)

    adxl.setInactivityXYZ(1, 0, 0);     // Set to detect inactivity in all the axes "adxl.setInactivityXYZ(X, Y, Z);" (1 == ON, 0 == OFF)
    adxl.setInactivityThreshold(75);    // 62.5mg per increment   // Set inactivity // Inactivity thresholds (0-255)
    adxl.setTimeInactivity(10);         // How many seconds of no activity is inactive?

    adxl.setTapDetectionOnXYZ(0, 0, 1); // Detect taps in the directions turned ON "adxl.setTapDetectionOnX(X, Y, Z);" (1 == ON, 0 == OFF)

    // Set values for what is considered a TAP and what is a DOUBLE TAP (0-255)
    adxl.setTapThreshold(50);           // 62.5 mg per increment
    adxl.setTapDuration(15);            // 625 μs per increment
    adxl.setDoubleTapLatency(80);       // 1.25 ms per increment
    adxl.setDoubleTapWindow(200);       // 1.25 ms per increment

    // Set values for what is considered FREE FALL (0-255)
    adxl.setFreeFallThreshold(7);       // (5 - 9) recommended - 62.5mg per increment
    adxl.setFreeFallDuration(30);       // (20 - 70) recommended - 5ms per increment

    // Setting all interupts to take place on INT1 pin
    //adxl.setImportantInterruptMapping(1, 1, 1, 1, 1);     // Sets "adxl.setEveryInterruptMapping(single tap, double tap, free fall, activity, inactivity);"
                                                        // Accepts only 1 or 2 values for pins INT1 and INT2. This chooses the pin on the ADXL345 to use for Interrupts.
                                                        // This library may have a problem using INT2 pin. Default to INT1 pin.

    // Turn on Interrupts for each mode (1 == ON, 0 == OFF)
    adxl.InactivityINT(0);
    adxl.ActivityINT(0);
    adxl.FreeFallINT(0);
    adxl.doubleTapINT(1);
    adxl.singleTapINT(0);
    adxl.watermarkINT(0); // enable watermark interrupt
    adxl.setInterruptMapping(ADXL345_INT_WATERMARK_BIT, ADXL345_INT2_PIN);

    //attachInterrupt(digitalPinToInterrupt(pinADXL_INT2), ADXL_ISR2, RISING);   // Attach Interrupt
    attachInterrupt(digitalPinToInterrupt(pinADXL_INT1), ADXL_ISR, RISING);   // Attach Interrupt
    // put device in FIFO mode, attach an interrupt to watermark bit to service FIFO
    // put FIFO servicing code into ISR
    //adxl.setFifoMode(ADXL345_FIFO_FIFO, ADXL_FIFO_THR, ADXL345_FIFO_INT2);
    //adxl.setRate(3200);//6.25);
    adxl.setFullResBit(true); // seems not to do anything in 2G mode which makes sense given datasheet
    delay(10);
    Serial.print("Rate: ");
    Serial.println(adxl.getRate());
    Serial.print("FIFOMODE: ");
    Serial.println(adxl.getFifoMode(),HEX);
    Serial.print("LOW POWER: ");
    if(adxl.isLowPower())
        Serial.println("ON");
    else
        Serial.println("OFF");
    delay(10);
    if(adxl.isInterruptEnabled(ADXL345_INT_WATERMARK_BIT)){
        Serial.println("WATERMARK ENABLED");
    } else {
        Serial.println("WATERMARK DISABLED");
    }
    Serial.print("INT SOURCE: ");
    Serial.println(adxl.getInterruptSource(),HEX);
    Serial.print("INT MAPPING: ");
    Serial.println(adxl.getInterruptMapping(ADXL345_INT_WATERMARK_BIT),HEX);
    //adxl345 is by default in full power mode,
    //watermark interrupt is enabled on INT2

    // read the ADXL345 FIFO until it's empty to prime the loop. Otherwise doesn't work
    // due to rising edge Interrupt race condition
    int16_t x_arr[32];
    int16_t y_arr[32];
    int16_t z_arr[32];

    for(int i = 0; i < 32; i++){
        adxl.readAccel(&x_arr[0], &y_arr[0], &z_arr[0]);
    }
}

//////////////////////////////////////////////
///////// INTERRUPT SERVICE ROUTINES /////////
//////////////////////////////////////////////
FASTRUN void adc0_isr()
{ // this triggers when conversion is complete
    adc->adc0->readSingle(); // readSingle clears interrupt
}

FASTRUN void adc1_isr()
{ // this triggers when conversion is complete on ADC1
    adc->adc1->readSingle(); // clear interrupt
}

FASTRUN void pdb_isr()
{   // pdb interrupt is enabled in case you need it.
    PDB0_SC &= ~PDB_SC_PDBIF; // clears interrupt
}

FASTRUN void dmaBuffer0_isr()
{
    if(current_channel == 0)
    {
        accel_read_sample_flag = true;
    }
    volatile uint16_t adc_sample_in = (uint16_t) dmaBuffer0->buffer()[0];
    samples[buffer_num][current_channel][samples_idx[current_channel]] = adc_sample_in;// Store most recent ADC val into Ping-Pong Buffer
    HandleNewEcgSampleDac(current_channel, adc_sample_in);
    samples_idx[current_channel] = (samples_idx[current_channel] + 1) % CHANNEL_BUFFER_LENGTH; // Move samples buffer indices

    // If an entire buffer has just filled up then switch buffers and set the flag to process the full buffer
    if ( (current_channel == (NUM_ECG_CHANNELS - 1)) && (samples_idx[current_channel] == 0))
    {
        buffer_num = (buffer_num == 1) ? 0 : 1; // Switch buffer_num between 0 and 1
        if(buffer_ready_flag){ Serial.println("BUFFER OVERRUN!"); }
        buffer_ready_flag = true;
    }
    current_channel = (current_channel + 1) % NUM_ECG_CHANNELS;
    switchNextMuxChannel(current_channel); // this used to be at the end of dmaBuffer0_isr but don't know why it wasnt earlier
    dacWriteNextChannel(current_channel); // Write the drive value for the next channel to DAC0
    dmaBuffer0->dmaChannel->clearInterrupt(); // Update the internal buffer positions
}
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
